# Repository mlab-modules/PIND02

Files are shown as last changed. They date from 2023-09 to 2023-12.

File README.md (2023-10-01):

# PIND02 - Solid-state semiconductor radiation detector

The PIN diode semiconductor detector for ionizing radiation. 

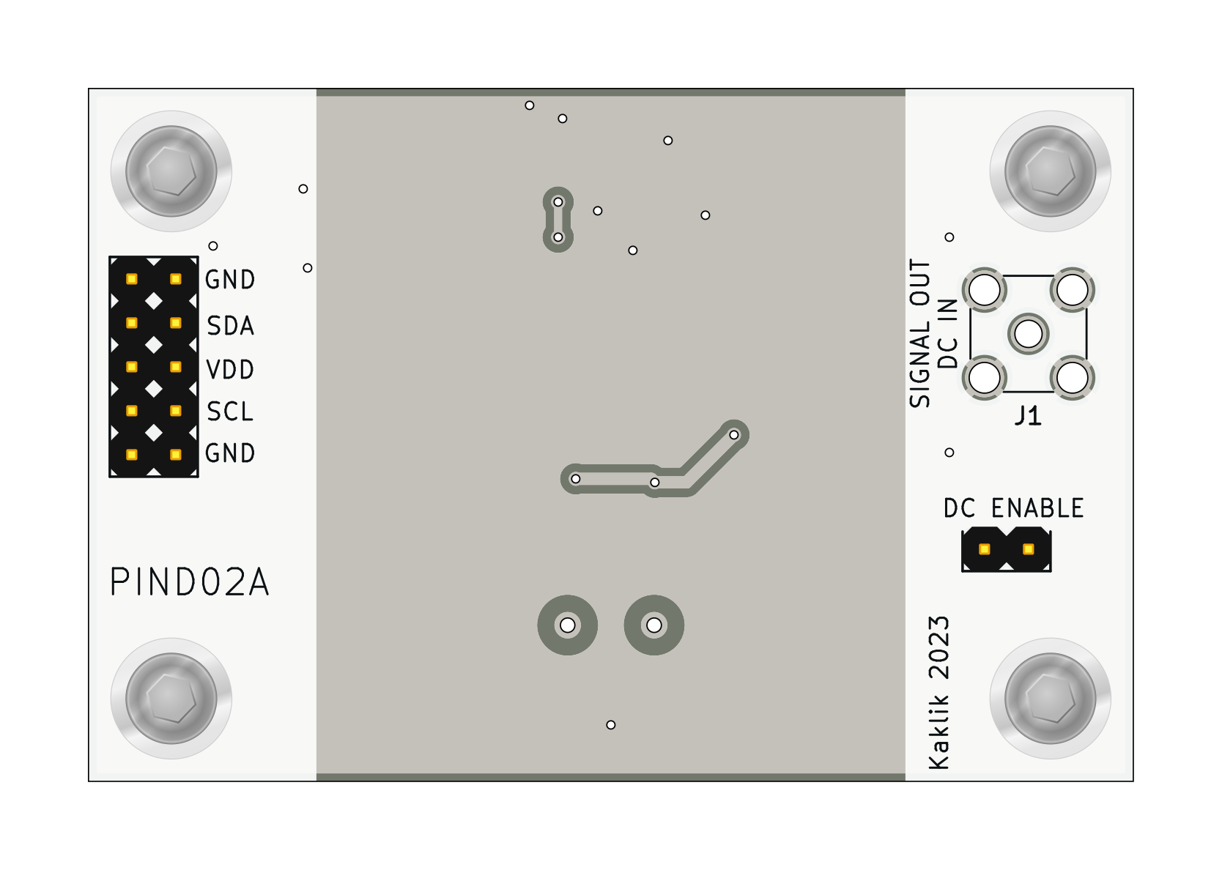
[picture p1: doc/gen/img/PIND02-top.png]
PIND02 view from the top

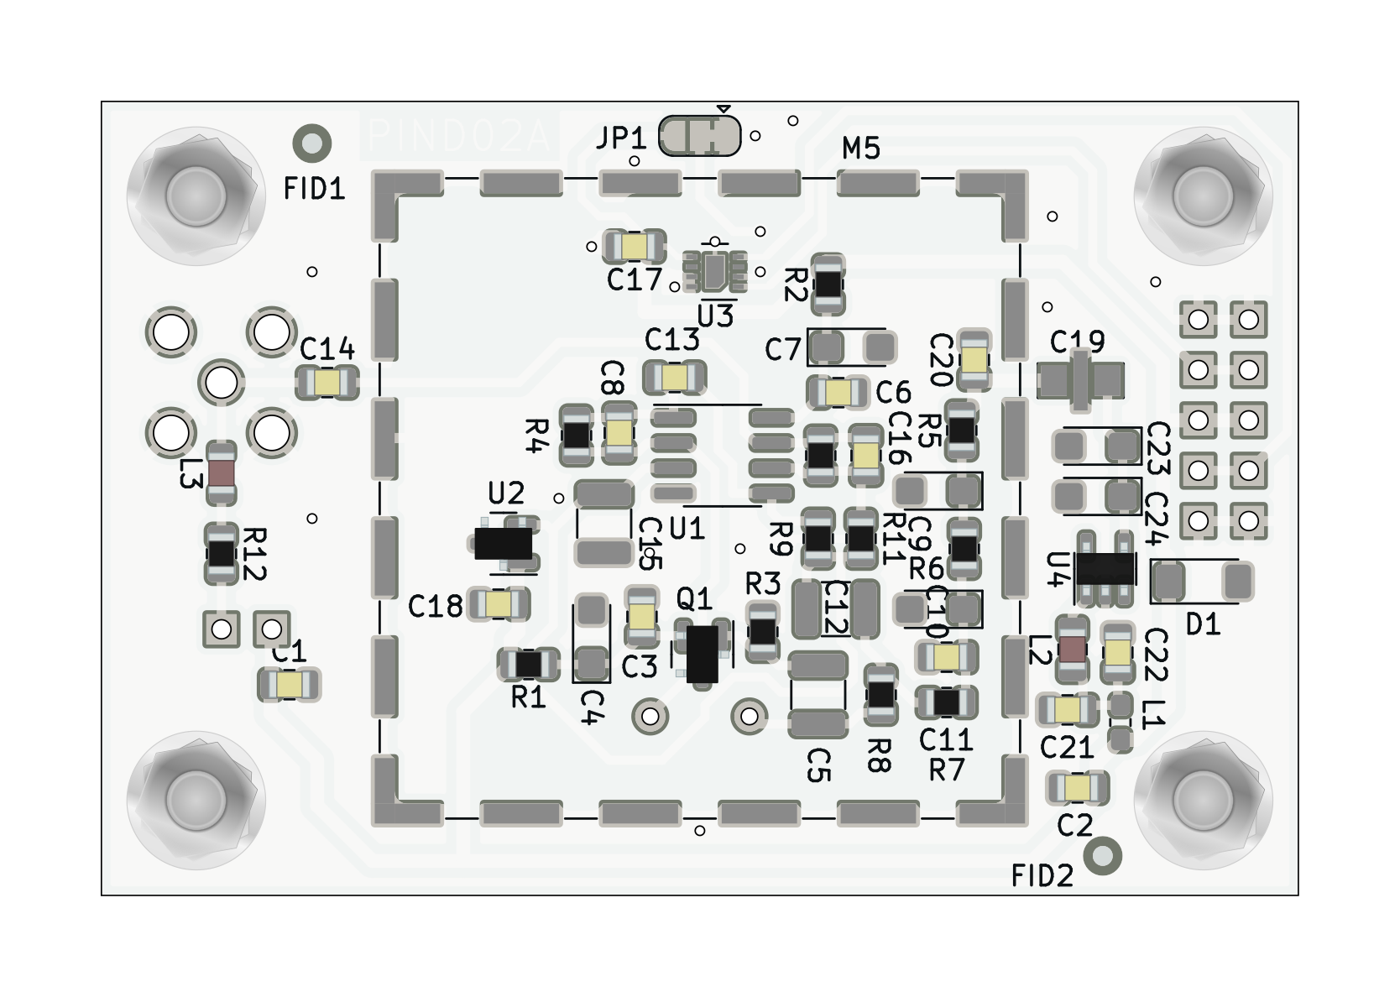
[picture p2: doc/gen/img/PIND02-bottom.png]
PIND02 bottom view


## Main features
  - sensitivity to a wide range of ionizing radiation types (charged particles, ions, photons, etc.)
  - Low-power consumtion
  - lightweight

## Basic usage

The module outputs pulses, which need to be digitized for computer processing. The suitable hardware for that task is [PCRD07](https://github.com/mlab-modules/PCRD07)

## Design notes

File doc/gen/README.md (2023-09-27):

# PCB

Board size: 60.45x40.13 mm (2.38x1.58 inches)

- This is the size of the rectangle that contains the board
- Thickness: 1.6 mm (63 mils)
- Material: FR4
- Finish: None
- Layers: 2
- Copper thickness: 35 µm

Solder mask: TOP / BOTTOM

- Color: Green

Silk screen: TOP / BOTTOM

- Color: White

Stackup:

| Name                 | Type                 | Color            | Thickness | Material        | Epsilon_r | Loss tangent |
|----------------------|----------------------|------------------|-----------|-----------------|-----------|--------------|
| F.SilkS              | Top Silk Screen      |                  |           |                 |           |              |
| F.Paste              | Top Solder Paste     |                  |           |                 |           |              |
| F.Mask               | Top Solder Mask      |                  |        10 |                 |           |              |
| F.Cu                 | copper               |                  |        35 |                 |           |              |
| dielectric 1         | core                 |                  |      1510 | FR4             |       4.5 |        0.020 |
| B.Cu                 | copper               |                  |        35 |                 |           |              |
| B.Mask               | Bottom Solder Mask   |                  |        10 |                 |           |              |
| B.Paste              | Bottom Solder Paste  |                  |           |                 |           |              |
| B.SilkS              | Bottom Silk Screen   |                  |           |                 |           |              |

# Important sizes

Clearance: 0.2 mm (8 mils)

Track width: 0.2 mm (8 mils)

- By design rules: 0.2 mm (8 mils)

Drill: 0.5 mm (20 mils)

- Vias: 0.5 mm (20 mils) [Design: 0.4 mm (16 mils)]
- Pads: 0.85 mm (33 mils)
- The above values are real drill sizes, they add 0.1 mm (4 mils) to plated holes (PTH)

Via: 0.8/0.4 mm (31/16 mils)

- By design rules: 0.4/0.3 mm (16/12 mils)
- Micro via: yes [0.2/0.1 mm (8/4 mils)]
- Buried/blind via: yes
- Total: 17 (thru: 17 buried/blind: 0 micro: 0)

Outer Annular Ring: 0.15 mm (6 mils)

- By design rules: 0.23 mm (9 mils)

Eurocircuits class: 4B
- Using min drill 0.5 mm for an OAR of 0.15 mm

# General stats

Components count: (SMD/THT)

- Top: 1/7 (SMD + THT)
- Bottom: 47/1 (SMD + THT)

Defined tracks:

- 0.2 mm (8 mils)
- 0.3 mm (12 mils)
- 0.4 mm (16 mils)
- 0.5 mm (20 mils)
- 0.6 mm (24 mils)
- 0.7 mm (28 mils)
- 0.8 mm (31 mils)

Used tracks:

- 0.2 mm (8 mils) (8) defined: yes
- 0.3 mm (12 mils) (13) defined: yes
- 0.4 mm (16 mils) (18) defined: yes
- 0.45 mm (18 mils) (159) defined: no
- 0.7 mm (28 mils) (51) defined: yes

Defined vias:

Used vias:

- 0.8/0.4 mm (31/16 mils) (Count: 17, Aspect: 2.0 A) defined: no

Holes (excluding vias):

- 0.76 mm (30 mils) (2)
- 0.89 mm (35 mils) (12)
- 1.5 mm (59 mils) (1)
- 1.7 mm (67 mils) (4)
- 3.0 mm (118 mils) (4)

Oval holes:

Drill tools (including vias and computing adjusts and rounding):

- 0.5 mm (20 mils) (17)
- 0.85 mm (33 mils) (2)
- 1.0 mm (39 mils) (12)
- 1.6 mm (63 mils) (1)
- 1.8 mm (71 mils) (4)
- 3.1 mm (122 mils) (4)

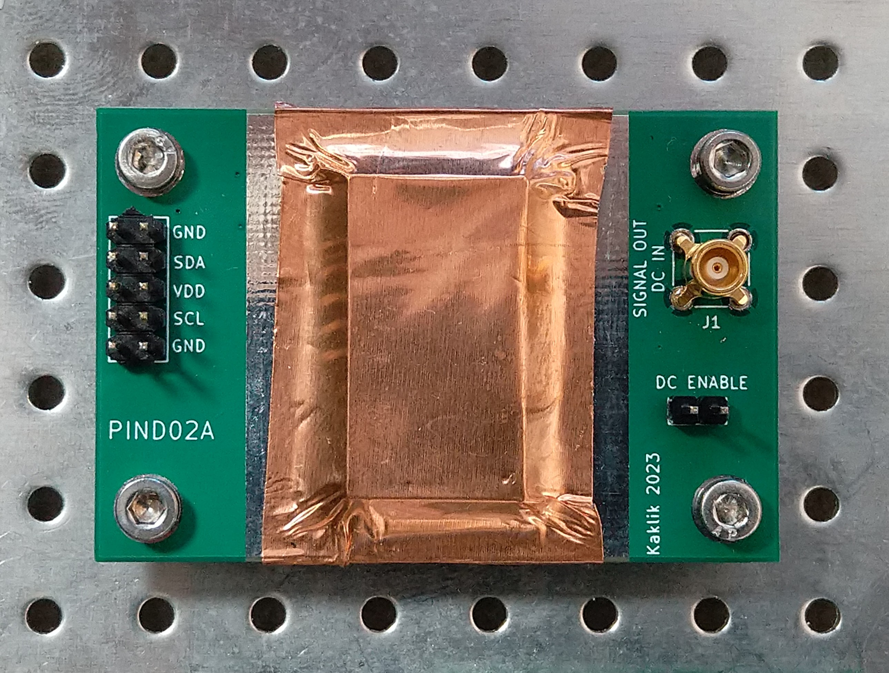
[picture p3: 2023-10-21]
doc/src/img/PIND02_top_big.jpg

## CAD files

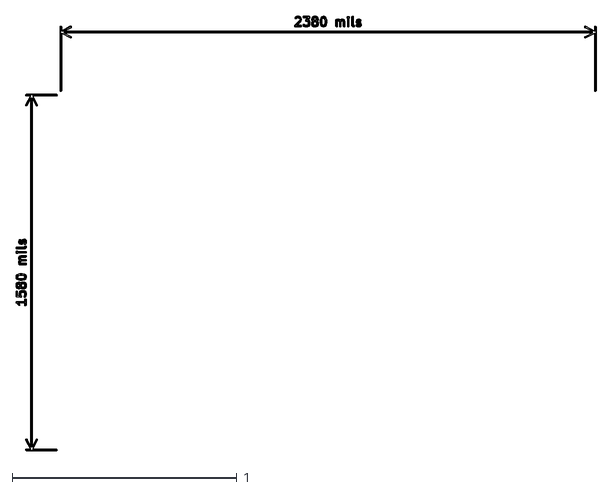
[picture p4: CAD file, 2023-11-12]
doc/gen/dxf/PIND02-User_Comments.dxf
2.58 x 1.93

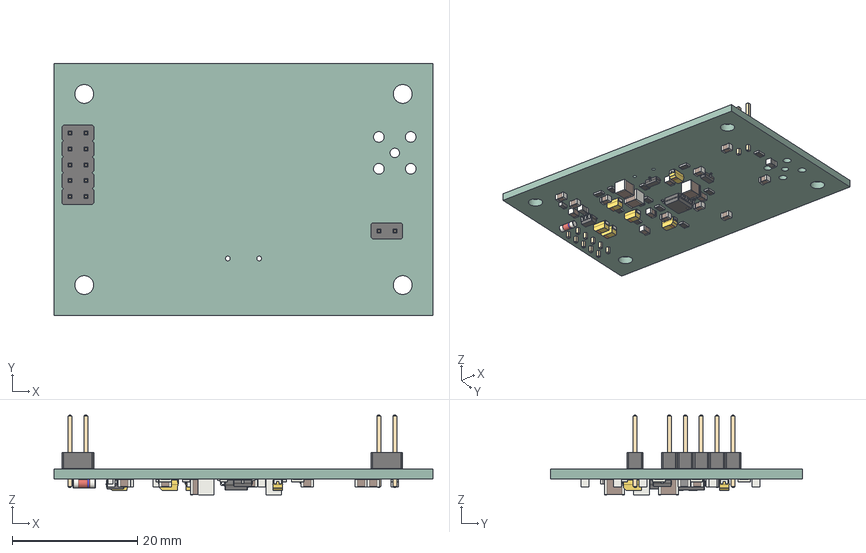
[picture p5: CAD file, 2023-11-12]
doc/gen/PIND02.step
60.5 x 40.1 x 12.7 mm
tmpj7qmsqgi PCB

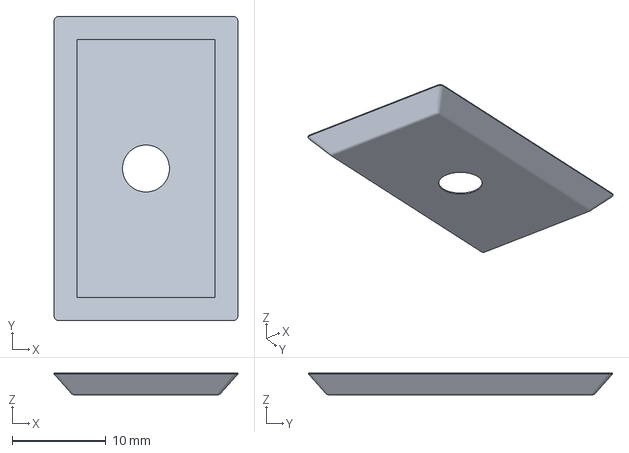
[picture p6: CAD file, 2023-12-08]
hw/cad/sensor_frame.3mf
19.6 x 32.4 x 2.32 mm

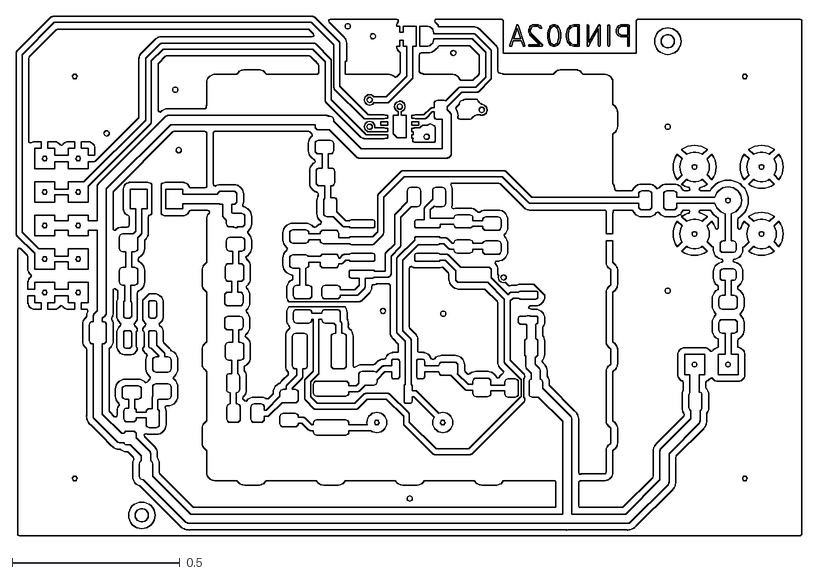
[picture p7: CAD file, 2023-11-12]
doc/gen/dxf/PIND02-B_Cu.dxf
2.35 x 1.55

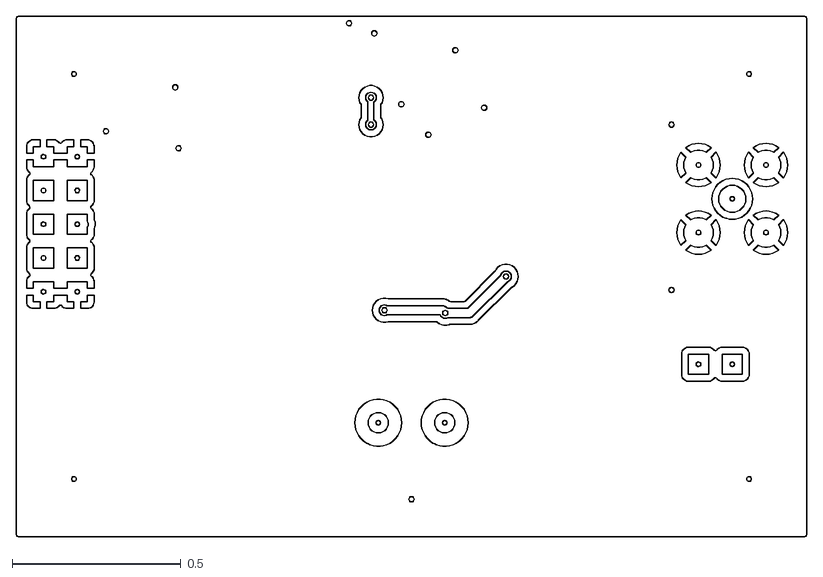
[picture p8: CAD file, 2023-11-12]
doc/gen/dxf/PIND02-F_Cu.dxf
2.34 x 1.54

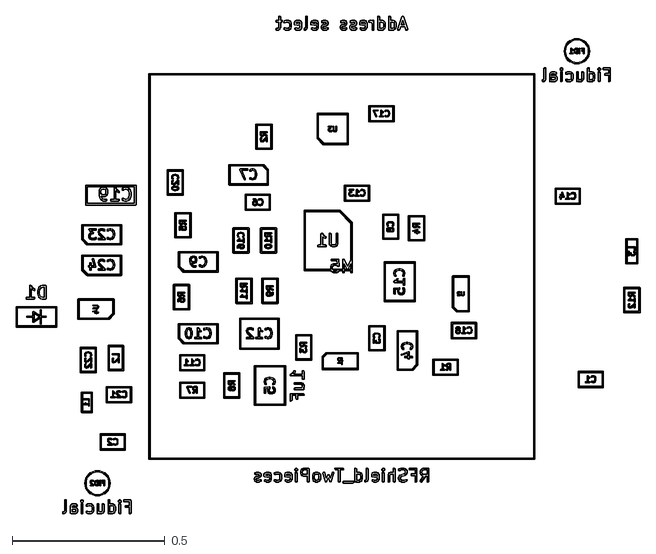
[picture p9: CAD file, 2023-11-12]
doc/gen/dxf/PIND02-B_Fab.dxf
2.04 x 1.63

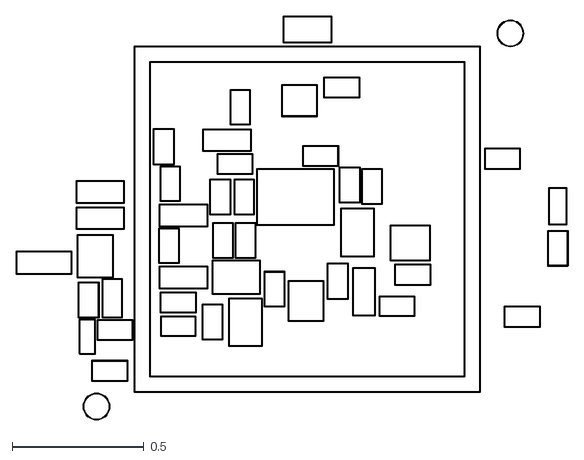
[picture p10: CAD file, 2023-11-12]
doc/gen/dxf/PIND02-B_Courtyard.dxf
2.09 x 1.53

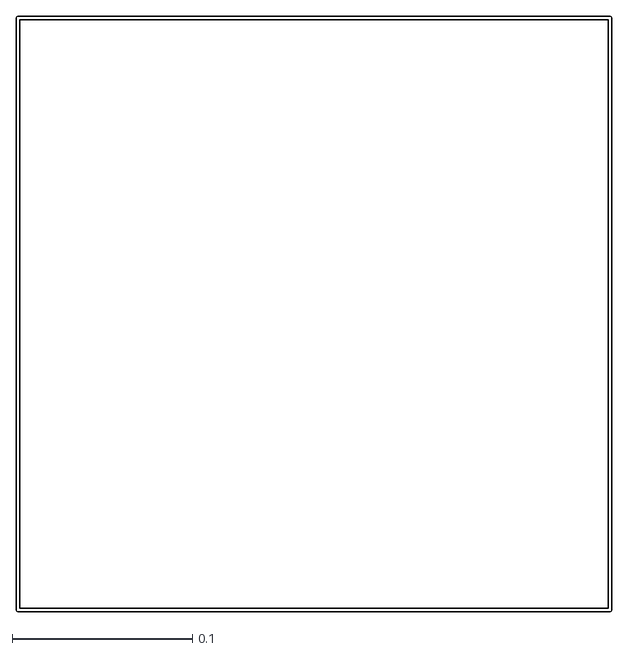
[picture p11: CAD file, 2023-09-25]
doc/gen/dxf/PIND02-F_Courtyard.dxf
0.33 x 0.33

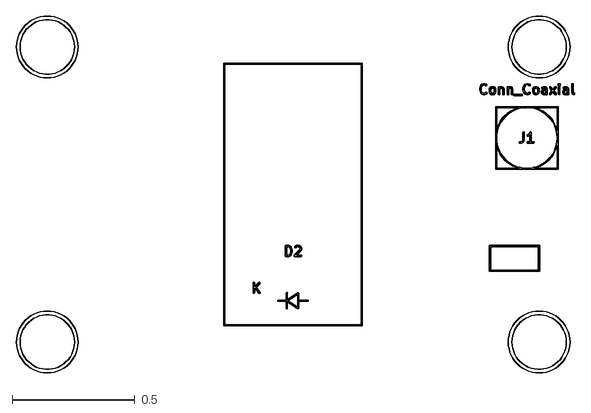
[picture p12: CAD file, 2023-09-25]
doc/gen/dxf/PIND02-F_Fab.dxf
2.27 x 1.45

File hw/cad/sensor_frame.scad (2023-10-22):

$fn=100;
clearance = 0.5;

sensor_width = 14.2;
sensor_lenght = 27.0;
sensor_height = 2.2;
layer_thickness = 0.3; 

module sensor_frame(){
  difference(){
      hull(){
        translate([0,0,clearance])
          minkowski(){
            cube([sensor_width + 2*clearance, sensor_lenght+ 2*clearance, sensor_height-4*clearance + layer_thickness],center=true);
            sphere(r = clearance);
          }
        translate([0,0,-sensor_height/2 + clearance/20])
          minkowski(){
            cube([sensor_width + 2*sensor_height, sensor_lenght + 2*sensor_height, clearance/10], center=true);
            translate([0,0,clearance/20]) cylinder(r = clearance, h = clearance/10);
          }
      }
      cube([sensor_width + clearance, sensor_lenght + clearance, sensor_height],center=true);
      cylinder(h=sensor_height, d=5,center=false);
  }
}

sensor_frame();

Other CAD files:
doc/gen/dxf/PIND02-User_5.dxf
doc/gen/dxf/PIND02-User_8.dxf
doc/gen/dxf/PIND02-Margin.dxf
doc/gen/dxf/PIND02-User_3.dxf
doc/gen/dxf/PIND02-User_2.dxf
doc/gen/dxf/PIND02-F_Adhesive.dxf
doc/gen/dxf/PIND02-B_Adhesive.dxf
doc/gen/dxf/PIND02-User_Eco2.dxf
doc/gen/dxf/PIND02-User_Eco1.dxf
doc/gen/dxf/PIND02-B_Mask.dxf
doc/gen/dxf/PIND02-B_Paste.dxf
doc/gen/dxf/PIND02-B_Silkscreen.dxf
doc/gen/dxf/PIND02-F_Mask.dxf
doc/gen/dxf/PIND02-F_Paste.dxf
doc/gen/dxf/PIND02-F_Silkscreen.dxf
doc/gen/dxf/PIND02-User_1.dxf
doc/gen/dxf/PIND02-User_4.dxf
doc/gen/dxf/PIND02-User_6.dxf
doc/gen/dxf/PIND02-User_7.dxf
doc/gen/dxf/PIND02-User_9.dxf
doc/gen/dxf/PIND02-User_Drawings.dxf
hw/cad/sensor_frame.stl

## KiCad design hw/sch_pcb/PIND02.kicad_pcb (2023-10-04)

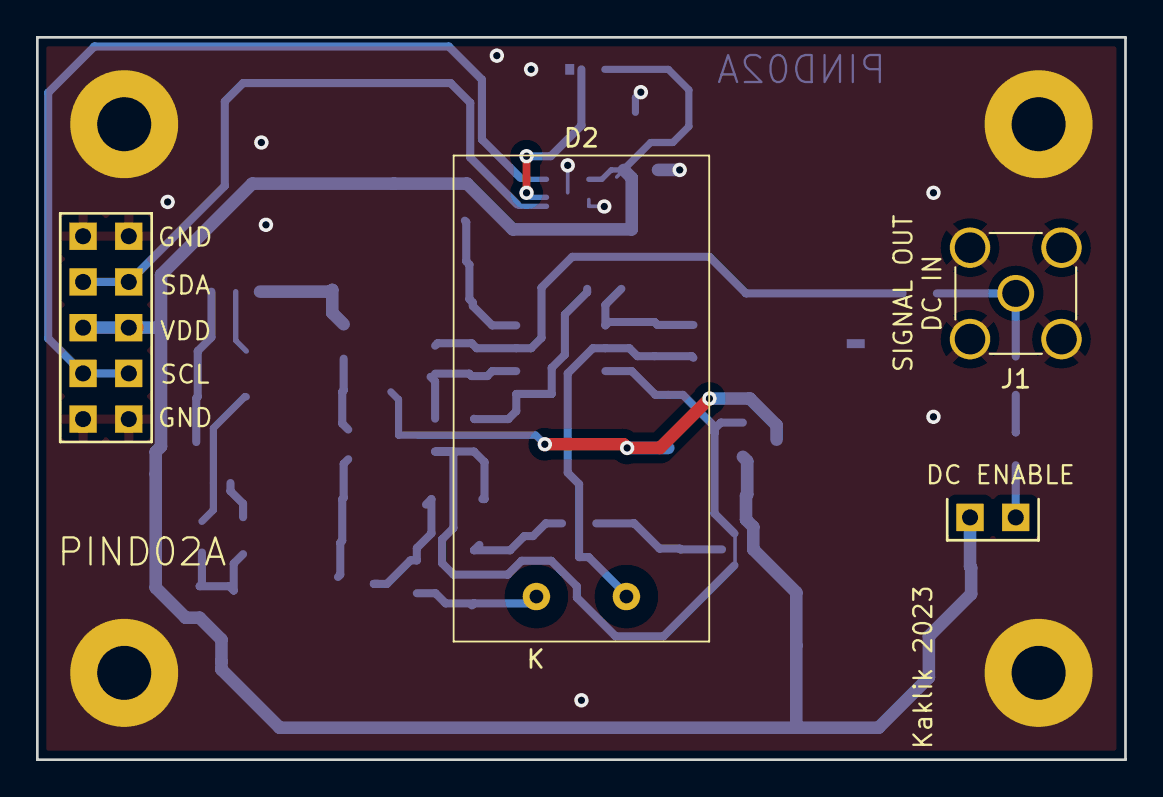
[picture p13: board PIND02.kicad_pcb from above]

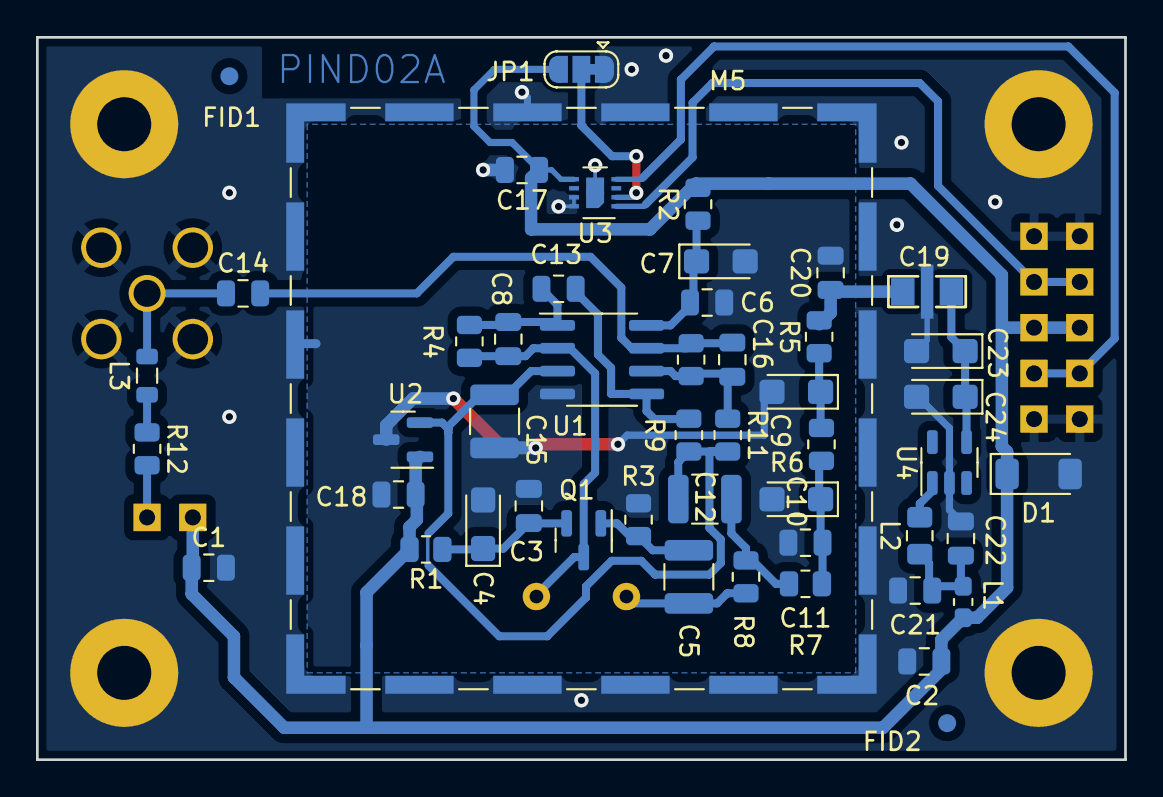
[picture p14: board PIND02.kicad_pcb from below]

Board: 2 copper layers, 60.5 x 40.1 mm, 58 parts (50 on the bottom side), 26 nets.

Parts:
C1, C21: 10uF; C_0805_2012Metric
C2, C3, C6, C11, C13, C14, C17, C18, C20, C22: 100nF; C_0805_2012Metric
C4, C7, C9, C10, C23, C24: 10uF; CP_EIA-3216-18_Kemet-A
C5, C12, C15: 1uF; C_1210_3225Metric
C8: 1pF/NP0 251R15S1R0AV4E; C_0805_2012Metric
C16: 3n3; C_0805_2012Metric
C19: NFM21PC105-1uF; FIR_0805
D1: BZV55C-6,2V; D_MiniMELF
D2: S2744-09; HAMAMATSU_S2744-09
FID1, FID2: Fiducial; Fiducial_1mm_Mask2mm
J1: Conn_Coaxial; SMA_Amphenol_901-144_Vertical
J2: MLAB I2C interface; Straight_2x05
J3: HEADER_2x01; Straight_2x01
JP1: Address select; SolderJumper-3_P1.3mm_Bridged12_RoundedPad1.0x1.5mm
JP2: Jumper_2_Bridged; NetTie-2_SMD_Pad0.5mm
L1: NL03KT330; L_0603_1608Metric_Pad1.05x0.95mm_HandSolder
L2: DFE252012P-4R7M; L_0805_2012Metric_Pad1.15x1.40mm_HandSolder
L3: L; L_0805_2012Metric
M1, M2: HOLE M3; MountingHole_3mm
M3, M4: HOLE; MountingHole_3mm
M5: RFShield_TwoPieces; Laird_Technologies_BMI-S-204-F_32.00x32.00mm
Q1: 2SK2394-6; SOT-23
R1, R2: 470R; R_0805_2012Metric
R3, R5, R6, R7, R8, R10: 4k7; R_0805_2012Metric
R4: 10M; R_0805_2012Metric
R9: 10k; R_0805_2012Metric
R11: 1k; R_0805_2012Metric
R12: 100; R_0805_2012Metric
U1: OPA2314; SOIC-8_3.9x4.9mm_P1.27mm
U2: ISL21080DIH312Z-TK; SOT-23
U3: SHT31-DIS; Sensirion_DFN-8-1EP_2.5x2.5mm_P0.5mm_EP1.1x1.7mm
U4: TPS613222ADBV; SOT-23-5

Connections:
+5V: C19.3, C20.1, R5.2
/A: C8.2, D2.2 (A), Q1.3 (G), R4.2, U1.2 (-)
/K: C5.2, D2.1 (K), R8.1
/REF: C12.2, C15.1, R9.1, R11.2, U1.3 (+), U2.2 (Vout)
GND: C1.2, C2.2, C17.2, C19.2, C21.2, C22.2, C23.2, C24.2, D1.2 (A), J1.2 (Ext), J2.1, J2.2, J2.9, J2.10, JP1.1 (A), JP2.2, M1.1, M2.1, M3.1, M4.1, M5.1 (Shield), U3.7 (R), U3.8 (VSS), U3.9 (VSS), U4.2 (GND)
GNDA: C3.2, C4.2, C6.2, C7.2, C9.2, C10.2, C11.2, C15.2, C18.2, C20.2, JP2.1, R3.2, U1.4 (V-), U2.3 (GND)
unnamed: C9.1, R5.1, R6.2
unnamed: C10.1, C11.1, R6.1, R7.2
unnamed: C12.1, R7.1, R8.2
unnamed: C8.1, C13.2, R4.1, U1.1
unnamed: C14.2, C16.1, R10.1, U1.7
unnamed: C21.1, C22.1, L1.2, L2.1
unnamed: C14.1, J1.1 (In), L3.2
unnamed: J3.2, R12.2
unnamed: JP1.2 (C), U3.2 (ADDR)
unnamed: L3.1, R12.1
unnamed: C3.1, C4.1, Q1.2 (D), R1.1
unnamed: C5.1, Q1.1 (S), R3.1
unnamed: C13.1, R9.2, U1.5 (+)
unnamed: C16.2, R10.2, R11.1, U1.6 (-)
unnamed: C6.1, C7.1, R2.1, U1.8 (V+)
unnamed: J2.7, J2.8, U3.4 (SCL)
unnamed: J2.3, J2.4, U3.1 (SDA)
unnamed: L2.2, U4.1 (SW)
unnamed: C19.1, C23.1, C24.1, U4.4 (VOUT)
VDD: C1.1, C2.1, C17.1, C18.1, D1.1 (K), J2.5, J2.6, J3.1, JP1.3 (B), L1.1, R1.2, R2.2, U2.1 (Vin), U3.5 (VDD)

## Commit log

2023-09-10 Initial schematics of PIN semiconductor ionising radiation sensor.
    [PIND02.kicad_pcb, PIND02.kicad_sch]
2023-09-10 Update actions products
    [PIND02-B_Adhesive.dxf, PIND02-B_Courtyard.dxf, PIND02-B_Cu.dxf, PIND02-B_Fab.dxf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]
2023-09-10 Update title block Resolve ERC errors.
    [PIND02.kicad_sch]
2023-09-24 Assing footprints to components. Starting of PCB design.
    [PIND02.kicad_pcb, PIND02.kicad_sch]
2023-09-24 PCB design WIP.
    [PIND02.kicad_pcb, PIND02.kicad_sch]
2023-09-25 The first fully routed PCB.
    [PIND02.kicad_pcb, PIND02.kicad_sch]
2023-09-25 Add silcreen texts.
    [PIND02.kicad_pcb]
2023-09-26 Add board dimensions.
    [PIND02.kicad_pcb]
2023-09-26 Improve protection diode type and footprint.
    [PIND02.kicad_sch]
2023-09-26 Routed PCB.
    [PIND02.kicad_pcb]
2023-09-27 Add solder mask keepout zone. Resolve #1.
    [PIND02.kicad_pcb]
2023-09-27 Kontrola a upravy pred vyrobou
    [PIND02.kicad_pcb]
2023-10-02 Edit UST_ID
    [PIND02.kicad_sch]
2023-10-04 Edit B.Fab
    [PIND02.kicad_pcb]
2023-10-11 Adding the sensor frame design.
    [sensor_frame.3mf, sensor_frame.scad, sensor_frame.stl]
2023-10-16 Increase gain.
    [PIND02.kicad_sch]
2023-10-22 Cover sensing area with one printed layer.
    [sensor_frame.3mf, sensor_frame.scad, sensor_frame.stl]
2023-11-12 Update measured values.
    [PIND02.kicad_sch]
2023-12-08 Set layer height to 0.2mm.
    [sensor_frame.3mf, sensor_frame.stl]
